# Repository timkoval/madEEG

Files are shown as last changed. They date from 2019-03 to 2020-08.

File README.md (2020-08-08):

# madEEG

This project is a fork and rebirth of an old project called "[OpenEEG](http://openeeg.sourceforge.net/doc/)".

The main feature of this project is that it uses currently available SMD components. Moreover, in the future I'm planning to try to make it cheaper using DSP instead of amplifier filters where it is possible.

I wanted to make it myself as a pet project, but unfortunately I don't have enough time and money. However, I really want this project to be developed... You are welcome to contribute!

## Requirements and tools

Schematic and PCB - [KiCAD](https://kicad-pcb.org/) 

Firmware - [STM32CubeIDE](https://www.st.com/en/development-tools/stm32cubeide.html) or any other IDE/code editor (As for me, I've recently migrated from CubeIDE to [VSCodium](https://vscodium.com/))

 Software - haven't thought about it yet, open to suggestions.

## Installation

No need to install project, just clone it, develop and contribute :) 

## Contributing

Pull requests are welcome! For major changes, please open an issue first to discuss what you would like to change.

## Authors

- **Tim Koval** - *Initial work* - [madTRACER](https://github.com/madTRACER)

## License

This project is under the MIT license.

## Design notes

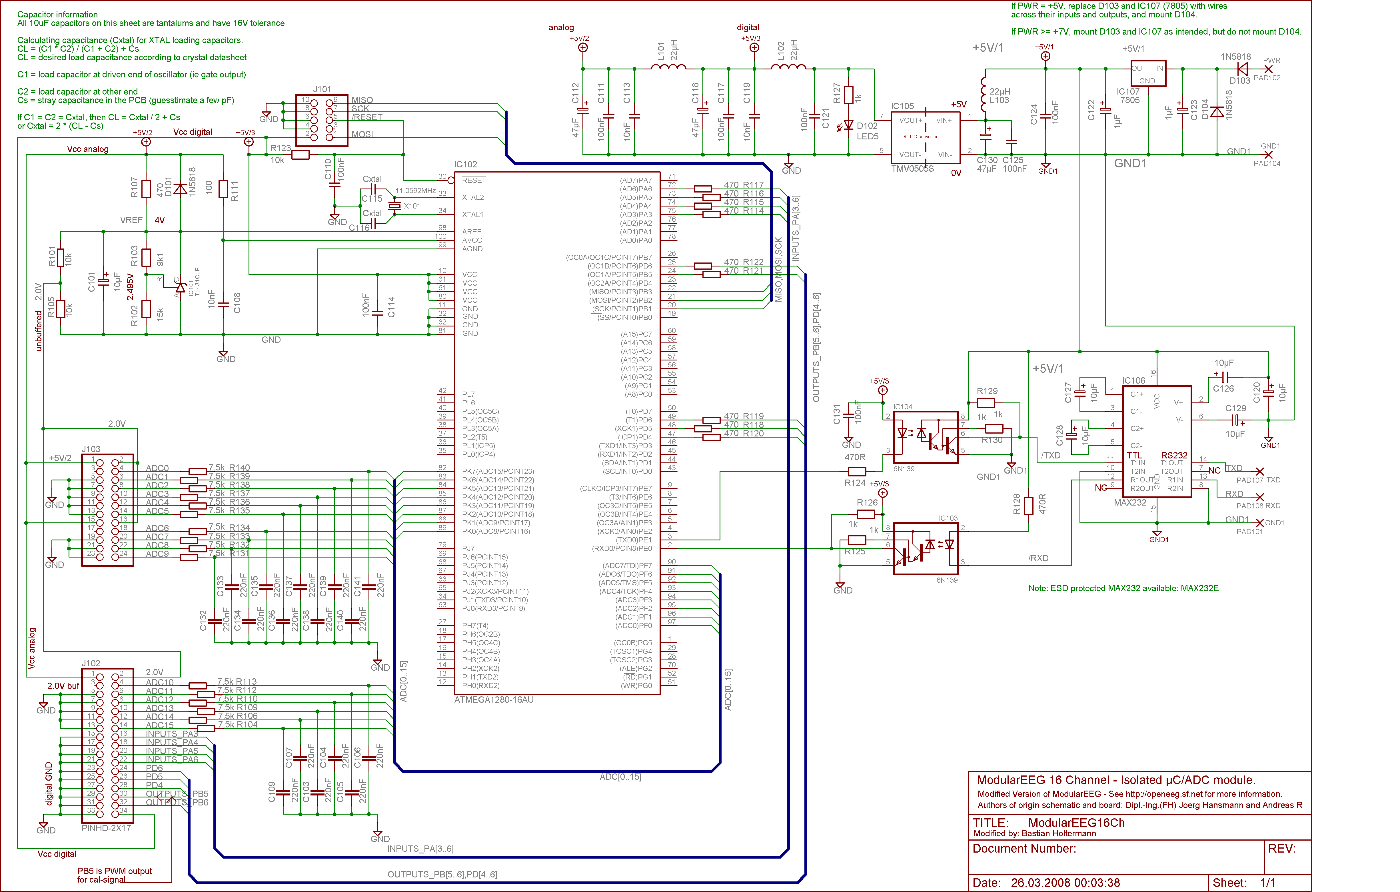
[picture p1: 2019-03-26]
REFERENCE/modeeg16ch - bastianholtermann.de - ModEEG16ch/ModularEEG16Ch.sch.png

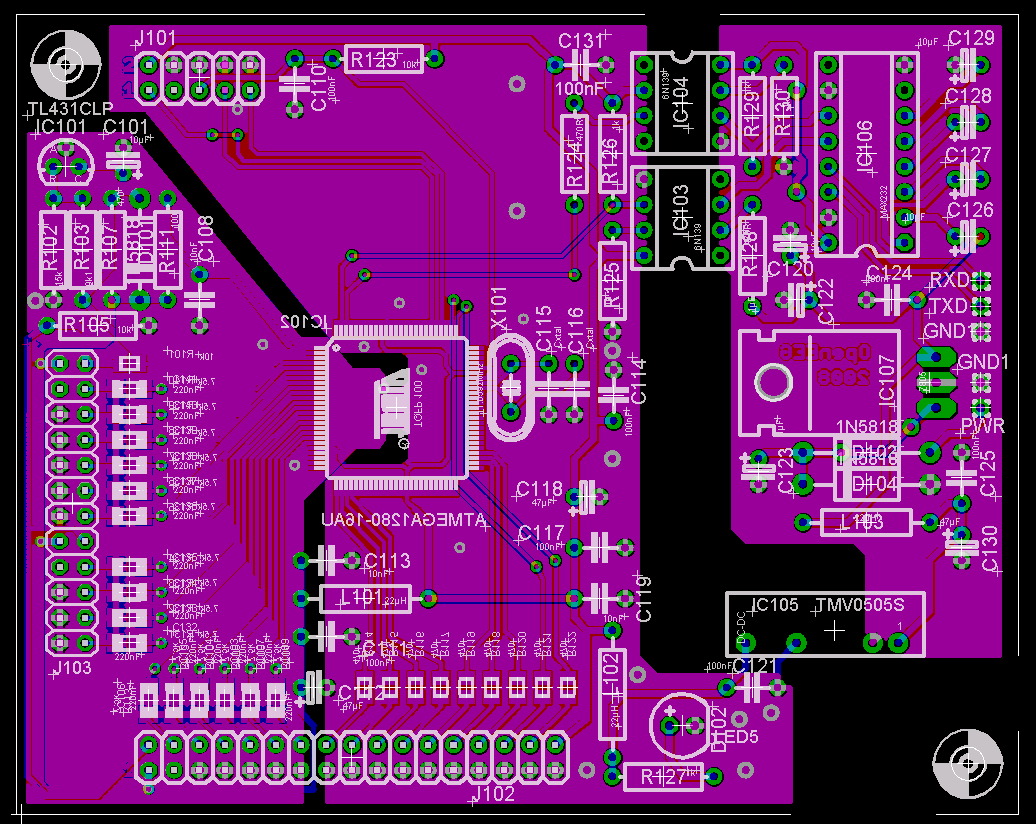
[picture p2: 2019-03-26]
REFERENCE/modeeg16ch - bastianholtermann.de - ModEEG16ch/ModularEEG16Ch.brd.png

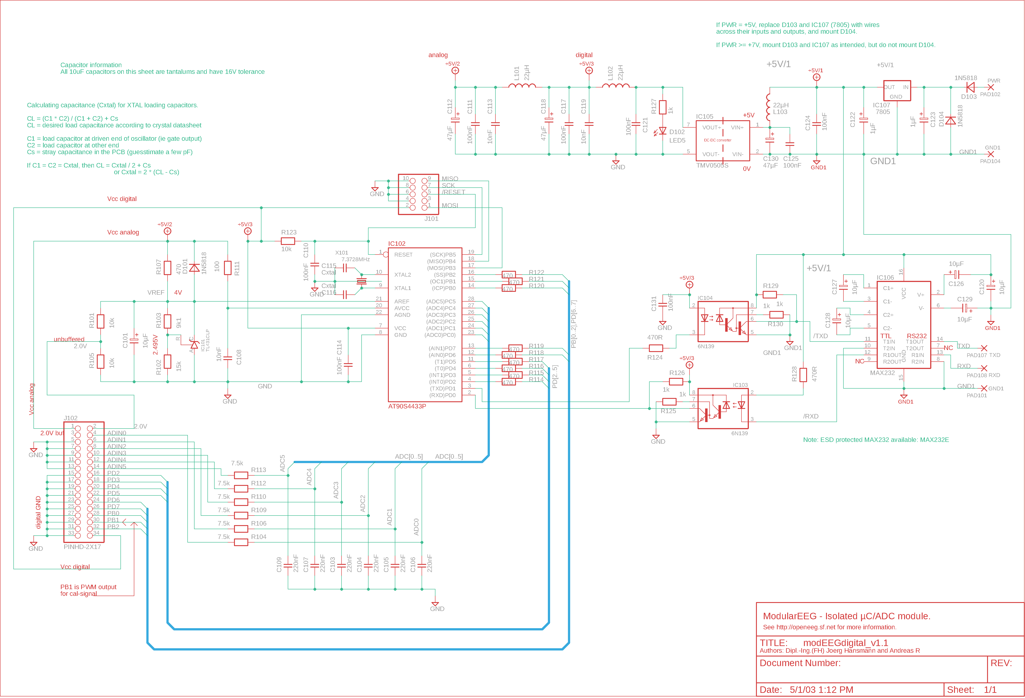
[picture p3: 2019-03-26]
REFERENCE/ModularEEG-v1.1.1/modEEGdigital_v1.1.png

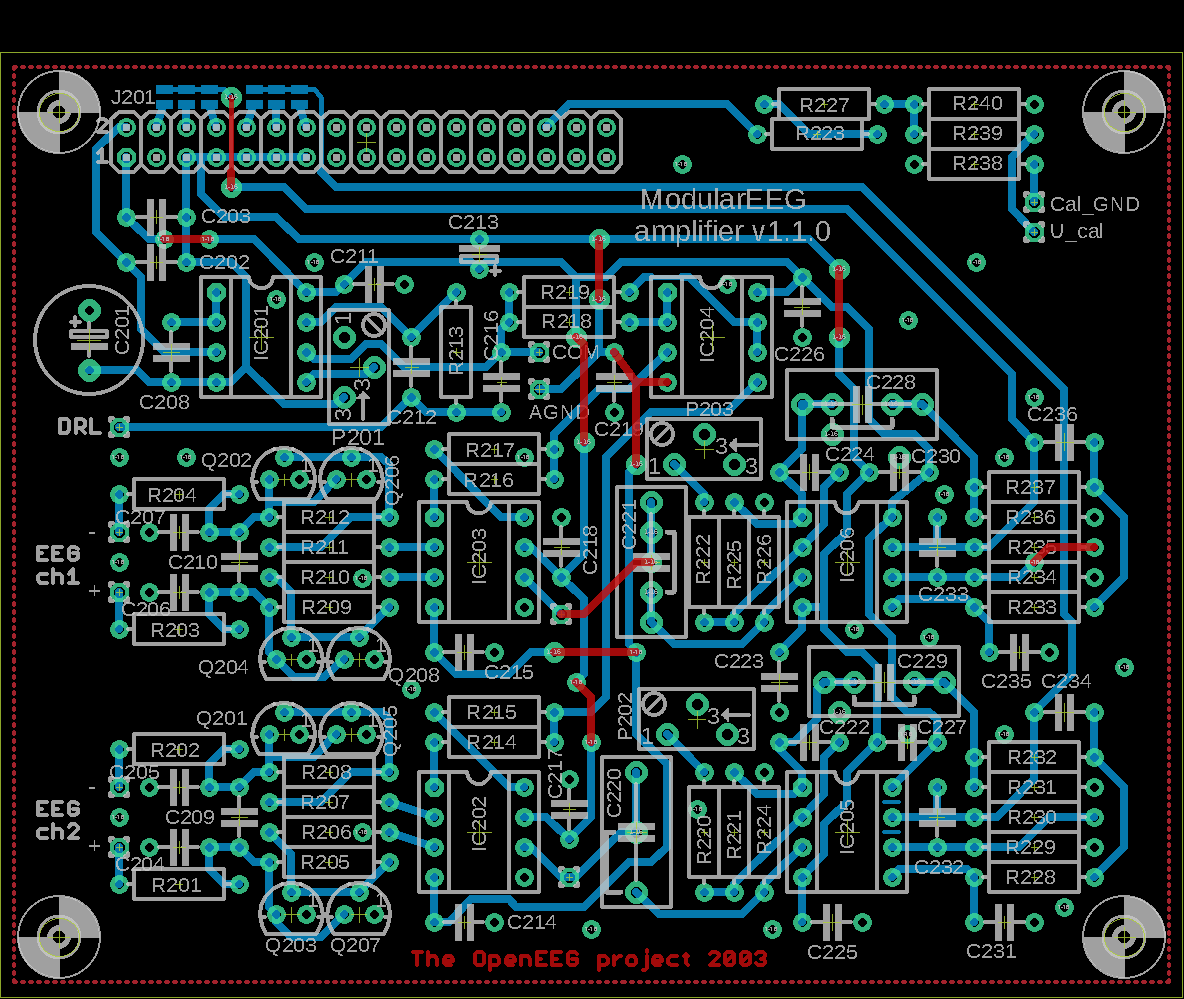
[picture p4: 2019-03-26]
REFERENCE/ModularEEG-v1.1.1/modEEGamp_v1.1_pcb.png

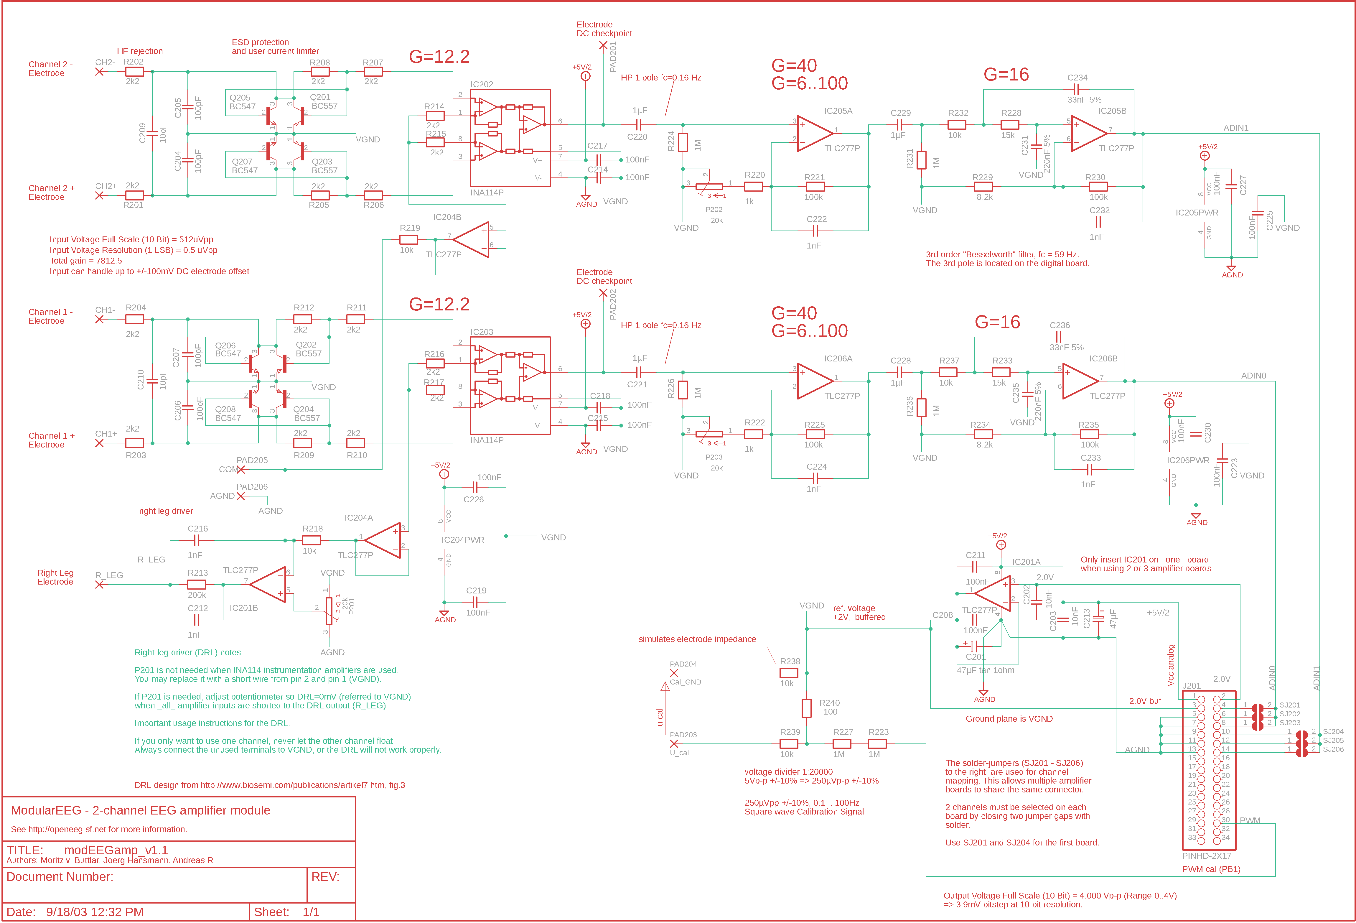
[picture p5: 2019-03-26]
REFERENCE/ModularEEG-v1.1.1/mogEEGamp_v1.1.png

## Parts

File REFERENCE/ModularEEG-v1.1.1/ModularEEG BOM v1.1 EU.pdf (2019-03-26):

# ModularEEG v1.1.0 - Bill of Materials

# Digital board

Qty | Value | Package | Parts

# Capacitors

1 | 27pF C0G | C-5 | C102
2 | Cxtal | C-5 | C115 | C116
3 | 10nF X7R | C-5 | C108 | C113 | C119
7 | 100nF X7R | C-5 | C110 | C111 | C114 | C117 | C121 | C124 | C125 | C131
6 | 220nF 5% | C-5 | C103 | C104 | C105 | C106 | C107 | C109
2 | 1µF tantalum | EL25B | C122 | C123
6 | 10µF tantalum | EL25B | C101 | C120 | C126 | C127 | C128 | C129
3 | 47µF tantalum | EL25B | C112 | C118 | C130

# Resistors

1 | 100R | R-10 | R111
12 | 470R | R-10 | R107 | R114 | R115 | R116 | R117 | R118 | R119 | R120 | R121 | R122 | R124 | R128
5 | 1k | R-10 | R125 | R126 | R127 | R129 | R130
6 | 7.5k | R-10 | R104 | R106 | R109 | R110 | R112 | R113
1 | 9k1 | R-10 | R103
3 | 10k | R-10 | R101 | R105 | R123
1 | 15k | R-10 | R102

# Discrete Semiconductors

3 | 1N5818 | D-12,5 | D101 | D103 | D104
1 | LED 5mm | LED5 | D102

# Integrated Circuits

2 | 6N139 | DIL-08 | IC103 | IC104
1 | 7805 | 78XXL_S | IC107
1 | AT90S4433P | DIL-28/3 | IC102
1 | MAX232 | DIL-16 | IC106
1 | TL431CLP | TO92-CLP | IC101
1 | TMV0505S | TMADCDC IC105

# Miscellaneous Parts

1 | 7.3728MHz | HC49/S | X101
3 | 22µH | R-12,5 | L101 | L102 | L103
1 | PINHD-2X5 | 2X05 | J101
1 | PINHD-2X17 | 2X17 | J102

# Analog board

Qty | Value | Package | Parts

# Capacitors

2 | 10pF C0G | C-5 | C209 | C210
4 | 100pF C0G | C-5 | C204 | C205 | C206 | C207
6 | 1nF X7R | C-5 | C212 | C216 | C222 | C224 | C232 | C233
2 | 10nF X7R | C-5 | C202 | C203
2 | 33nF 5% | C-5 | C234 | C236
12 | 100nF X7R | C-5 | C208 | C211 | C214 | C215 | C217 | C218 | C219 | C223 | C225 | C226 | C227 | C230
2 | 220nF 5% | C-5 | C231 | C235
4 | 1µF film | C-10 | C220 | C221 | C228 | C229
1 | 47µF tantalum | EL25B | C213
1 | 47µF tan 1ohm | ES-5 | C201

# Resistors

1 | 100R | R-10 | R240
2 | 1k | R-10 | R220 | R222
16 | 2k2 | R-10 | R201 | R202 | R203 | R204 | R205 | R206 | R207 | R208 | R209 | R210 | R211 | R212
| | | R214 | R215 | R216 | R217
2 | 8.2k | R-10 | R229 | R234
6 | 10k | R-10 | R218 | R219 | R232 | R237 | R238 | R239
2 | 15k | R-10 | R228 | R233
4 | 100k | R-10 | R221 | R225 | R230 | R235
1 | 200k | R-10 | R213
6 | 1M | R-10 | R223 | R224 | R226 | R227 | R231 | R236

# Discrete Semiconductors

4 | BC547 | TO92 | Q205 | Q206 | Q207 | Q208
4 | BC557 | TO92 | Q201 | Q202 | Q203 | Q204

# Integrated Circuits

2 | INA114P | DIL-08 | IC202 | IC203
4 | TLC277P | DIL-08 | IC201 | IC204 | IC205 | IC206

# Miscellaneous Parts

3 | 20k | S64Y | P201 | P202 | P203
1 | PINHD-2X17 | 2X17 | J201

170

# ModularEEG v1.1.0 - ordering information

All prices as of September 2002.

See notes below. No part is selected. See distributor-specific notes below.. Not available. Prices given are estimates.

| Reichelt | RS Components | Reichelt | RS Components

Color key:

Value | Package | Qty
D
| | | Qty
A
| | | | Qty D+A

Qty

| | | | | D+2A | Part requirements and notes | Part no. | Unit Price | Min
Qty | ? | Part no.
| | | | | | | | | | | Unit Price | Min
Qty | ?
| | | | | | | | | | | | | | Qty
D
| | | | | | | | | | | | | | | Qty
A
| | | | | | | | | | | | | | | | Qty D+A

Qty

| | | | | | | | | | | | | | | | | D+2A | Price
D
| | | | | | | | | | | | | | | | | | | Price
A
| | | | | | | | | | | | | | | | | | | | Price D+A | Price D+2A | Qty
D
| | | | | | | | | | | | | | | | | | | | | | | Qty
A
| | | | | | | | | | | | | | | | | | | | | | | | Qty D+A

Qty

| | | | | | | | | | | | | | | | | | | | | | | | | D+2A | Price
D
| | | | | | | | | | | | | | | | | | | | | | | | | | | Price A | Price D+A | Price D+2A
Capacitors | | | | | | | | | | | | | Capacitors
10pF C0G | C-5 | | 2 | 2 | 4 | 100V, 5mm pitch,C0G | Kerko-500 10p | 0,07 | 1 | N/A | 0,1 | 5 | 10pF C0G | | 2 | 2 | 4 | | 0,14 | 0,14 | 0,28 | | 5 | 5 | 5 | | 0,5 | 0,5 | 0,5
Cxtal C0G | C-5 | 2 | 2 | 2 5mm pitch, C0G. See notes. | Kerko-500 56p | 0,07 | 1 1 | N/A | 0,1 | 5 1 | Cxtal C0G | 2 | 2 | 2 | 0,14 | 0,14 | 0,14 | 5 | 5 | 5 | 0,5 | 0,5 | 0,5
100pF C0G | C-5 | | 4 | 4 | 8 | 100V, 5mm pitch, C0G | Kerko-500 100p | 0,07 | 1 | N/A | 0,1 | 5 | 100pF C0G | | 4 | 4 | 8 | | 0,28 | 0,28 | 0,56 | | 5 | 5 | 10 | | 0,5 | 0,5 | 1
1nF X7R | C-5 | | 6 | 6 | 12 | 200V, 5mm pitch, X7R | X7R-5 1,0n | 0,07 | 1 | 298-9028 | 0,14 | 5 | 1nF X7R | | 6 | 6 | 12 | | 0,42 | 0,42 | 0,84 | | 10 | 10 | 15 | | 1,4 | 1,4 | 2,1
10nF X7R | C-5 | 3 | 2 | 5 | 7 | 100V, 5mm pitch, X7R | X7R-5 10n | 0,07 | 1 | 264-4832 | 0,16 | 5 | 10nF X7R | 3 | 2 | 5 | 7 | 0,21 | 0,14 | 0,35 | 0,49 | 5 | 5 | 5 | 10 | 0,8 | 0,8 | 0,8 | 1,6
33nF 5% | C-5 | | 2 | 2 | 4 | 5%, 5mm pitch, max 3.5mm wide | N/A | 0,1 | 1 | 312-1504 | 0,082 | 10 | 33nF 5% | | 2 | 2 | 4 | | 0,2 | 0,2 | 0,4 | | 10 | 10 | 10 | | 0,82 | 0,82 | 0,82
100nF X7R | C-5 | 8 | 12 | 20 | 32 | 50V, 5mm pitch, X7R | X7R-5 100n | 0,12 | 1 | 264-4876 | 0,205 | 5 | 100nF X7R | 8 | 12 | 20 | 32 | 0,96 | 1,44 | 2,4 | 3,84 | 10 | 15 | 20 | 35 | 2,05 | 3,075 | 4,1 | 7,175
220nF 5% | C-5 | 6 | 2 | 8 | 10 | 5%, 5mm pitch, max 3.5mm wide | N/A | 0,2 | 1 | 312-1475 | 0,139 | 10 | 220nF 5% | 6 | 2 | 8 | 10 | 1,2 | 0,4 | 1,6 | 2 | 10 | 10 | 10 | 10 | 1,39 | 1,39 | 1,39 | 1,39
1µF film | C-10 | | 4 | 4 | 8 | 5% tolerance, 10mm pitch | MKH100-10 1,0µ | 0,3 | 1 | 298-0188 | 0,349 | 5 | 1µF film | | 4 | 4 | 8 | | 1,2 | 1,2 | 2,4 | | 5 | 5 | 10 | | 1,745 | 1,745 | 3,49
1µF tantalum | EL25B | 2 | | 2 | 2 | 35V, 2.5mm pitch | TANTAL 1,0/35 | 0,15 | 1 | N/A | 0,2 | 1 | 1µF tantalum | 2 | | 2 | 2 | 0,3 | | 0,3 | 0,3 | 2 | | 2 | 2 | 0,4 | | 0,4 | 0,4
10µF tantalum | EL25B | 6 | | 6 | 6 | 16V, 2.5mm pitch | TANTAL 10/16 | 0,22 | 1 | N/A | 0,2 | 1 | 10µF tantalum | 6 | | 6 | 6 | 1,32 | | 1,32 | 1,32 | 6 | | 6 | 6 | 1,2 | | 1,2 | 1,2
47µF tantalum | EL25B | 3 | 1 | 4 | 5 | > 6.3V, 2.5mm pitch | TANTAL 47/6,3 | 0,33 | 1 | N/A | 0,3 | 1 | 47µF tantalum | 3 | 1 | 4 | 5 | 0,99 | 0,33 | 1,32 | 1,65 | 3 | 1 | 4 | 5 | 0,9 | 0,3 | 1,2 | 1,5
47µF tan 1ohm | ES-5 | 1 | 1 | 2 > 6.3V, 5mm pitch, ESR = 0.8 - 1.2 ohm | N/A | 3 | 1 | N/A | 3 | 1 | 47µF tan 1ohm | 1 | 1 | 2 | 3 | 3 | 6 | 1 | 1 | 2 | 3 | 3 | 6
Resistors | | | | | | | | | | | | | Resistors
100R | R-10 | 1 | 1 | 2 | 3 | 1% metal film, 0.25W, 10mm pitch | METALL 100 | 0,08 | 1 | 148-269 | 0,044 | 10 | 100R | 1 | 1 | 2 | 3 | 0,08 | 0,08 | 0,16 | 0,24 | 10 | 10 | 10 | 10 | 0,44 | 0,44 | 0,44 | 0,44
470R | R-10 | 12 | | 12 | 12 | 1% metal film, 0.25W, 10mm pitch | METALL 470 | 0,08 | 1 | 148-427 | 0,044 | 10 | 470R | 12 | | 12 | 12 | 0,96 | | 0,96 | 0,96 | 20 | | 20 | 20 | 0,88 | | 0,88 | 0,88
1k | R-10 | 5 | 2 | 7 | 9 | 1% metal film, 0.25W, 10mm pitch | METALL 1,00K | 0,08 | 1 | 148-506 | 0,044 | 10 | 1k | 5 | 2 | 7 | 9 | 0,4 | 0,16 | 0,56 | 0,72 | 10 | 10 | 10 | 10 | 0,44 | 0,44 | 0,44 | 0,44
2k2 | R-10 | | 16 | 16 | 32 | 1% metal film, 0.25W, 10mm pitch | METALL 2,20K | 0,08 | 1 | 148-584 | 0,044 | 10 | 2k2 | | 16 | 16 | 32 | | 1,28 | 1,28 | 2,56 | | 20 | 20 | 40 | | 0,88 | 0,88 | 1,76
7.5k | R-10 | 6 | | 6 | 6 | 1% metal film, 0.25W, 10mm pitch | METALL 7,50K | 0,08 | 1 | 148-708 | 0,044 | 10 | 7.5k | 6 | | 6 | 6 | 0,48 | | 0,48 | 0,48 | 10 | | 10 | 10 | 0,44 | | 0,44 | 0,44
8.2k | R-10 | | 2 | 2 | 4 | 1% metal film, 0.25W, 10mm pitch | METALL 8,20K | 0,08 | 1 | 148-714 | 0,044 | 10 | 8.2k | | 2 | 2 | 4 | | 0,16 | 0,16 | 0,32 | | 10 | 10 | 10 | | 0,44 | 0,44 | 0,44
9k1 | R-10 | 1 | | 1 | 1 | 1% metal film, 0.25W, 10mm pitch | METALL 9,10K | 0,08 | 1 | 148-720 | 0,044 | 10 | 9k1 | 1 | | 1 | 1 | 0,08 | | 0,08 | 0,08 | 10 | | 10 | 10 | 0,44 | | 0,44 | 0,44
10k | R-10 | 3 | 6 | 9 | 15 | 1% metal film, 0.25W, 10mm pitch | METALL 10,0K | 0,08 | 1 | 148-736 | 0,044 | 10 | 10k | 3 | 6 | 9 | 15 | 0,24 | 0,48 | 0,72 | 1,2 | 10 | 10 | 10 | 20 | 0,44 | 0,44 | 0,44 | 0,88
15k | R-10 | 1 | 2 | 3 | 5 | 1% metal film, 0.25W, 10mm pitch | METALL 15,0K | 0,08 | 1 | 148-770 | 0,044 | 10 | 15k | 1 | 2 | 3 | 5 | 0,08 | 0,16 | 0,24 | 0,4 | 10 | 10 | 10 | 10 | 0,44 | 0,44 | 0,44 | 0,44
100k | R-10 | | 4 | 4 | 8 | 1% metal film, 0.25W, 10mm pitch | METALL 100K | 0,08 | 1 | 148-972 | 0,044 | 10 | 100k | | 4 | 4 | 8 | | 0,32 | 0,32 | 0,64 | | 10 | 10 | 10 | | 0,44 | 0,44 | 0,44
200k | R-10 | | 1 | 1 | 2 | 1% metal film, 0.25W, 10mm pitch | METALL 200K | 0,08 | 1 | 149-054 | 0,044 | 10 | 200k | | 1 | 1 | 2 | | 0,08 | 0,08 | 0,16 | | 10 | 10 | 10 | | 0,44 | 0,44 | 0,44
1M | R-10 | | 6 | 6 | 12 | 1% metal film, 0.25W, 10mm pitch | METALL 1,00M | 0,08 | 1 | 149-228 | 0,044 | 10 | 1M | | 6 | 6 | 12 | | 0,48 | 0,48 | 0,96 | | 10 | 10 | 20 | | 0,44 | 0,44 | 0,88
Discrete Semiconductors | | | | | | | | | | | | | Discrete Semiconductors
1N5818 | D-12,5 | 3 | | 3 | 3 | Any 1A schottky should work. | 1N 5818 | 0,06 | 1 | 348-5505 | 0,12 | 1 | | 1N5818 | 3 | | 3 | 3 | 0,18 | | 0,18 | 0,18 | 3 | | 3 | 3 | 0,36 | | 0,36 | 0,36
BC547 | TO92 | | 4 | 4 | 8 | TO92 | BC 547B | 0,05 | 1 | 348-9399 | 0,043 | 1 | | BC547 | | 4 | 4 | 8 | | 0,2 | 0,2 | 0,4 | | 4 | 4 | 8 | | 0,172 | 0,172 | 0,344
BC557 | TO92 | 4 | 4 | 8 | TO92 | BC 557B | 0,05 | 1 | 348-9456 | 0,043 | 1 | BC557 | 4 | 4 | 8 | 0,2 | 0,2 | 0,4 | 4 | 4 | 8 | 0,172 | 0,172 | 0,344
LED 5mm | LED5 | 1 | 1 | 1 | Any LED | 0,3 | 1 | 0,3 | 1 | LED 5mm | 1 | 1 | 1 | 0,3 | 0,3 | 0,3 | 1 | 1 | 1 | 0,3 | 0,3 | 0,3
Integrated Circuits | | | | | | | | | | | | Integrated Circuits
6N139 | DIL-08 | 2 | 2 | 2 | Optocoupler | 6N139 | 0,69 | 1 | 303-135 | 1,18 | 1 | | 6N139 | 2 | 2 | 2 | 1,38 | 1,38 | 1,38 | 2 | 2 | 2 | 2,36 | 2,36 | 2,36
7805 | 78XXL_S | 1 | 1 | 1 | 5V regulator, >= 500mA. Size TO220 | µA 7805 | 0,28 | 1 | 633-026 | 0,575 | 1 | 7805 | 1 | 1 | 1 | 0,28 | 0,28 | 0,28 | 1 | 1 | 1 | 0,575 | 0,575 | 0,575
AT90S4433P | DIL-28/3 | 1 | 1 | 1 Will be replaced by ATmega8 soon. | AT 90S4433 PDIP | 7,5 | 1 | N/A | 7,5 | 1 | AT90S4433P | 1 | 1 | 1 | 7,5 | 7,5 | 7,5 | 1 | 1 | 1 | 7,5 | 7,5 | 7,5
INA114AP | DIL-08 | 2 | 2 | 4 | Low-power precision inamp | INA 114AP | 7,85 | 1 2 | 311-524 | 7,86 | 1 | INA114AP | 2 | 2 | 4 | 15,7 | 15,7 | 31,4 | 2 | 2 | 4 | 15,72 | 15,72 | 31,44
MAX232 | DIL-16 | 1 | 1 | 1 | RS232 tranceiver | MAX 232 CPE | 1 | 1 3 | 225-8510 | 1,74 | 1 | MAX232 | 1 | 1 | 1 | 1 | 1 | 1 | 1 | 1 | 1 | 1,74 | 1,74 | 1,74
TL431CLP | TO92-CLP | 1 | 1 | 1 | Adjustable voltage reference | TL 431 ACLP | 0,3 | 1 | 267-9995 | 0,39 | 1 | TL431CLP | 1 | 1 | 1 | 0,3 | 0,3 | 0,3 | 1 | 1 | 1 | 0,39 | 0,39 | 0,39
TLC277P | DIL-08 | 4 | 4 | 7 Dual precision opamp | TLC 277 DIP | 1,65 | 1 | 428-464 | 1,785 | 1 | TLC277P | 4 | 4 | 7 | 6,6 | 6,6 | 11,55 | 4 | 4 | 7 | 7,14 | 7,14 | 12,5
TMV0505S | TMADCDC | 1 | 1 | 1 5Vin-5Vout 10% SIP7, 3kV iso | N/A | 10 | 1 | 192-0826 | 10,7 | 1 3 | TMV0505S | 1 | 1 | 1 | 10 | 10 | 10 | 1 | 1 | 1 | 10,7 | 10,7 | 10,7
Miscellaneous Parts | | | | | | | | | | | | Miscellaneous Parts
20k | S64Y | 3 | 3 | 6 | Multi-turn trimpot, 64Y footprint | 64Y-20K | 0,64 | 1 | 154-2448 | 1,476 | 1 | | 20k | 3 | 3 | 6 | 1,92 | 1,92 | 3,84 | 3 | 3 | 6 | 4,428 | 4,428 | 8,856
22µH | R-12,5 | 3 | 3 | 3 | SRF > 13MHz, Imax > 285mA, 12.5mm pitch | SMCC 22µ | 0,19 | 1 | 191-0526 | 0,225 | 10 | 22µH | 3 | 3 | 3 | 0,57 | 0,57 | 0,57 | 10 | 10 | 10 | 2,25 | 2,25 | 2,25
7.3728MHz | HC49/S | 1 | 1 | 1 HC49 or equivalent package. | 7,3728-HC49U-S | 0,49 | 1 1 | 311-811 | 1,23 | 1 1 | 7.3728MHz | 1 | 1 | 1 | 0,49 | 0,49 | 0,49 | 1 | 1 | 1 | 1,23 | 1,23 | 1,23
PINHD-2X17 | 2X17 | 1 | 1 | 2 | 3 2x17 pin-header / ribbon cable connector | STIFTL. 2X17G | 0,21 | 1 | 2 | PINHD-2X17 | 1 | 1 | 2 | 3 | 0,21 | 0,21 | 0,42 | 0,63
PINHD-2X5 | 2X05 | 1 | 1 | 1 2x5 pin-header / ribbon cable connector | STIFTL. 2X17G | 0,21 | 1 | 2 | PINHD-2X5 | 1 | 1 | 1 | 0,21 | 0,21 | 0,21
Sockets | | | | | | | | | | | | Sockets
8-pin socket | DIL-08 | 2 | 6 | 8 | 14 | GS 8 | 0,03 | 1 | Very expensive | 8-pin socket | 2 | 6 | 8 | 14 | 0,06 | 0,18 | 0,24 | 0,42
16-pin socket | DIL-16 | 1 | 1 | 1 | GS 16 | 0,04 | 1 | since minimum | 16-pin socket | 1 | 1 | 1 | 0,04 | 0,04 | 0,04
28-pin socket | DIL-28 | 1 | 1 | 1 | 7.68mm wide. | GS 14 | 0,04 | 2 4 | order is 50 pieces. | 28-pin socket | 2 | 2 | 2 | 0,08 | 0,08 | 0,08
Socket strip | SIL-20 | | | | Can be useful... | | | | 267-7400 | 0,55 | 5 | Socket strip

Notes

Crystal and loading capacitors (Cxtal)
The crystal's loading capacitors must be chosen appropriately. Set Cxtal = (Cload - Cstray) * 2
Cload (crystal loading capacitance) is given in the crystal data sheet. Cstray is stray capacitance on the PCB + microcontroller. Estimate Cstray = 3 - 5pF.

47uF 1 ohm capacitor
This capacitor is hard to locate in through-hole form (unless you order from Newark) You can replace it with an SMD type.
Mount an SMD like this: Solder the negative end to its pad. Have the positive end land on the ground plane. Scrape off the solder mask
in front of the positive end and solder.
Also note that any ESR = 0.8 ohm to 1.2 ohm is acceptable.

Microcontroller
The AT90S4433 is "not recommended for new designs" which is industry-speak for "we are not going to manufacture this part for much longer". The replacement is the ATmega8. However, it has a problem associated with it:
ADC channels 5 and 6 are only 8 bit, while the EEG board is designed with 10 bit resolution in mind. (Channels 1 - 4 are ok though.)

TLC277 amplifier
In a four channel EEG setup (two amplifier boards), you only mount IC201 on one board.

DCDC converter
TMV0505S is not available in many places. It can be replaced with NMV0505SA. This converter has a rather high output voltage (6-7 V) at very light loads. Therefore, when building the digital board, mount all parts except the microcontroller. Turn on the power and measure the voltage in the +5V/3 net, e.g. at IC103 pin 8. The voltage should be LESS than 6V. If not, you must reduce the value of R127 (near the LED), in order to present the DCDC converter with a higher load.

Pin headers
These are fairly expensive at RS (order code 531-942, you need 17x2 + 17x2 + 3x2 = 74 pins total) so try to find them elsewhere.
You need 2.54mm pitch double-row headers or equialent connectors, for ribbon cable. The ribbon cable can be made from an old floppy-drive cable.

Socket strip
Instead of soldering wires directly to the PCB's you can solder in socket strips which you have cut into suitable lengths.
Then insert the wires into the sockets without soldering, during the testing phase. This way you do not risk breaking the wires before putting everything securely in a box. (Then you should solder them in.) 0.5mm diameter single-strand wire is suitable.

Reichelt notes
1) Crystal loading capacitance is 32pF so Cxtal = 56pF (estimate Cstray = 4pF)
2) Higher grade is available: INA114BP which costs €13.60. Note that for this application this is hardly needed.
3) The MAX232 listed does not have ESD protected I/O pins. Protected type has part no MAX232 ECPE and costs €4.80.
4) Two 14-pin sockets

RS components notes
Prices were calculated from SEK to Euros by dividing by ten but at the time of writing 1 EUR = 9 SEK. Also, VAT is not included.
1) Crystal loading capacitance is 7pF so Cxtal = 10pF (estimate Cstray = 5 pF)
2) Avoid buying these parts from here. They are more expensive than they need to be.
3) TMV0505S is replaced by NMV0505SA

Newark Electronics notes
1) Crystal loading capacitance is 20pF so Cxtal = 33pF (estimate Cstray = 4pF)
2) The part has 2.5mm lead pitch - bend to 5mm
3) The part has 5mm lead pitch rather than 10mm. C220 can be mounted two ways. The lower placement (seen PCB layout) is the correct one.
4) This part may be replaced with a small aluminium electroytic. Part no 18C4465 for $0.063
5) Digital board capacitors can be replaced by an aluminium electrolytics. This may degrade noise immunity. (Probably not). Part no 18C4469 for $0.147
6) ESR=1.2 Ohm. Can be replaced with an ESR=1.0 Ohm type. Part no 87F5155 for $4.78
7)
8)
9) Higher grade INA114BP is available. Part no 35C1716 for $12.08
10) A cheaper alternative is MAX232 CPE that lacks ESD protection. Part no 34C3833 for $2.91
11) TMV0505S is replaced by NMV0505SA

Digi-Key notes
1) Carbon resistor for possibly improved ESR protection
2) Can be replaced with the newer generation ATMEGA8-16PI-ND $6.33 see Microcontroller note above.
3) Higher grade: INA114BP-ND $10.28
4) Or S2212-17-ND tin $1.77 - a special order item

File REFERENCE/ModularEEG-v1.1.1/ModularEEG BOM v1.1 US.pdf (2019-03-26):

# ModularEEG v1.1.0 - Bill of Materials

# Digital board

Qty | Value | Package | Parts

# Capacitors

1 | 27pF C0G | C-5 | C102
2 | Cxtal | C-5 | C115 | C116
3 | 10nF X7R | C-5 | C108 | C113 | C119
7 | 100nF X7R | C-5 | C110 | C111 | C114 | C117 | C121 | C124 | C125 | C131
6 | 220nF 5% | C-5 | C103 | C104 | C105 | C106 | C107 | C109
2 | 1µF tantalum | EL25B | C122 | C123
6 | 10µF tantalum | EL25B | C101 | C120 | C126 | C127 | C128 | C129
3 | 47µF tantalum | EL25B | C112 | C118 | C130

# Resistors

1 | 100R | R-10 | R111
12 | 470R | R-10 | R107 | R114 | R115 | R116 | R117 | R118 | R119 | R120 | R121 | R122 | R124 | R128
5 | 1k | R-10 | R125 | R126 | R127 | R129 | R130
6 | 7.5k | R-10 | R104 | R106 | R109 | R110 | R112 | R113
1 | 9k1 | R-10 | R103
3 | 10k | R-10 | R101 | R105 | R123
1 | 15k | R-10 | R102

# Discrete Semiconductors

3 | 1N5818 | D-12,5 | D101 | D103 | D104
1 | LED 5mm | LED5 | D102

# Integrated Circuits

2 | 6N139 | DIL-08 | IC103 | IC104
1 | 7805 | 78XXL_S | IC107
1 | AT90S4433P | DIL-28/3 | IC102
1 | MAX232 | DIL-16 | IC106
1 | TL431CLP | TO92-CLP | IC101
1 | TMV0505S | TMADCDC IC105

# Miscellaneous Parts

1 | 7.3728MHz | HC49/S | X101
3 | 22µH | R-12,5 | L101 | L102 | L103
1 | PINHD-2X5 | 2X05 | J101
1 | PINHD-2X17 | 2X17 | J102

# Analog board

Qty | Value | Package | Parts

# Capacitors

2 | 10pF C0G | C-5 | C209 | C210
4 | 100pF C0G | C-5 | C204 | C205 | C206 | C207
6 | 1nF X7R | C-5 | C212 | C216 | C222 | C224 | C232 | C233
2 | 10nF X7R | C-5 | C202 | C203
2 | 33nF 5% | C-5 | C234 | C236
12 | 100nF X7R | C-5 | C208 | C211 | C214 | C215 | C217 | C218 | C219 | C223 | C225 | C226 | C227 | C230
2 | 220nF 5% | C-5 | C231 | C235
4 | 1µF film | C-10 | C220 | C221 | C228 | C229
1 | 47µF tantalum | EL25B | C213
1 | 47µF tan 1ohm | ES-5 | C201

# Resistors

1 | 100R | R-10 | R240
2 | 1k | R-10 | R220 | R222
16 | 2k2 | R-10 | R201 | R202 | R203 | R204 | R205 | R206 | R207 | R208 | R209 | R210 | R211 | R212
| | | R214 | R215 | R216 | R217
2 | 8.2k | R-10 | R229 | R234
6 | 10k | R-10 | R218 | R219 | R232 | R237 | R238 | R239
2 | 15k | R-10 | R228 | R233
4 | 100k | R-10 | R221 | R225 | R230 | R235
1 | 200k | R-10 | R213
6 | 1M | R-10 | R223 | R224 | R226 | R227 | R231 | R236

# Discrete Semiconductors

4 | BC547 | TO92 | Q205 | Q206 | Q207 | Q208
4 | BC557 | TO92 | Q201 | Q202 | Q203 | Q204

# Integrated Circuits

2 | INA114P | DIL-08 | IC202 | IC203
4 | TLC277P | DIL-08 | IC201 | IC204 | IC205 | IC206

# Miscellaneous Parts

3 | 20k | S64Y | P201 | P202 | P203
1 | PINHD-2X17 | 2X17 | J201

170

# ModularEEG v1.1.0 - ordering information

All prices as of September 2002.

See notes below. No part is selected. See distributor-specific notes below.. Not available. Prices given are estimates.

| | | | | | | Newark Electronics | | Digi-Key (USD) | | | | Newark Electronics | | Digi-Key
Value | Package | Qty D | Qty A | Qty D+A | Qty D+2A | Part requirements and notes | Part no. | Unit Price | Min Qty | ? | Part no. | Unit Price | Min Qty | ? | | Qty D | Qty A | Qty D+A | Qty D+2A | Price D | Price A | Price D+A | Price D+2A | Qty D | Qty A | Qty D+A | Qty D+2A | Price D | Price A | Price D+A | Price D+2A

Color key:

Capacitors | | | | | | | | | | Capacitors
10pF C0G | C-5 | | 2 | 2 | 4 | 100V, 5mm pitch,C0G | 50N1022 | 0,044 | 1 | 10pF C0G | | 2 | 2 | 4 | | 0,088 | 0,088 | 0,176
Cxtal C0G | C-5 | 2 | 2 | 2 5mm pitch, C0G. See notes. | 50N1028 | 0,044 | 1 1 | Cxtal C0G | 2 | 2 | 2 | 0,088 | 0,088 | 0,088
100pF C0G | C-5 | | 4 | 4 | 8 | 100V, 5mm pitch, C0G | 50N1068 | 0,044 | 1 | 100pF C0G | | 4 | 4 | 8 | | 0,176 | 0,176 | 0,352
1nF X7R | C-5 | | 6 | 6 | 12 | 200V, 5mm pitch, X7R | 87F4719 | 0,142 | 1 2 | 1nF X7R | | 6 | 6 | 12 | | 0,852 | 0,852 | 1,704
10nF X7R | C-5 | 3 | 2 | 5 | 7 | 100V, 5mm pitch, X7R | 87F4724 | 0,123 | 1 | 10nF X7R | 3 | 2 | 5 | 7 | 0,369 | 0,246 | 0,615 | 0,861
33nF 5% | C-5 | | 2 | 2 | 4 | 5%, 5mm pitch, max 3.5mm wide | 18C4841 | 0,236 | 1 | 33nF 5% | | 2 | 2 | 4 | | 0,472 | 0,472 | 0,944
100nF X7R | C-5 | 8 | 12 | 20 | 32 | 50V, 5mm pitch, X7R | 96F8771 | 0,122 | 1 | 100nF X7R | 8 | 12 | 20 | 32 | 0,976 | 1,464 | 2,44 | 3,904
220nF 5% | C-5 | 6 | 2 | 8 | 10 | 5%, 5mm pitch, max 3.5mm wide | 95B5780 | 0,108 | 1 | 220nF 5% | 6 | 2 | 8 | 10 | 0,648 | 0,216 | 0,864 | 1,08
1µF film | C-10 | | 4 | 4 | 8 | 5% tolerance, 10mm pitch | 95B5792 | 0,325 | 1 3 | 1µF film | | 4 | 4 | 8 | | 1,3 | 1,3 | 2,6
1µF tantalum | EL25B | 2 | | 2 | 2 | 35V, 2.5mm pitch | 50N905 | 0,235 | 1 | 1µF tantalum | 2 | | 2 | 2 | 0,47 | | 0,47 | 0,47
10µF tantalum | EL25B | 6 | | 6 | 6 | 16V, 2.5mm pitch | 50N883 | 0,459 | 1 4 | 10µF tantalum | 6 | | 6 | 6 | 2,754 | | 2,754 | 2,754
47µF tantalum | EL25B | 3 | 1 | 4 | 5 | > 6.3V, 2.5mm pitch | 50N860 | 0,683 | 1 5 | 47µF tantalum | 3 | 1 | 4 | 5 | 2,049 | 0,683 | 2,732 | 3,415
47µF tan 1ohm | ES-5 | 1 | 1 | 2 > 6.3V, 5mm pitch, ESR = 0.8 - 1.2 ohm | 95F4832 | 2,96 | 1 6 | 47µF tan 1ohm | 1 | 1 | 2 | 2,96 | 2,96 | 5,92
Resistors | | | | | | | | | | | | | Resistors
100R | R-10 | 1 | 1 | 2 | 3 | 1% metal film, 0.25W, 10mm pitch | 84N1686 | 0,031 | 1 | | | | 100R | 1 | 1 | 2 | 3 | 0,031 | 0,031 | 0,062 | 0,093
470R | R-10 | 12 | | 12 | 12 | 1% metal film, 0.25W, 10mm pitch | 84N1765 | 0,031 | 1 | | | | 470R | 12 | | 12 | 12 | 0,372 | | 0,372 | 0,372
1k | R-10 | 5 | 2 | 7 | 9 | 1% metal film, 0.25W, 10mm pitch | 84N1712 | 0,031 | 1 | | | | 1k | 5 | 2 | 7 | 9 | 0,155 | 0,062 | 0,217 | 0,279
2k2 | R-10 | | 16 | 16 | 32 | 1% metal film, 0.25W, 10mm pitch | 84N1737 | 0,031 | 1 | | | | 2k2 | | 16 | 16 | 32 | | 0,496 | 0,496 | 0,992
7.5k | R-10 | 6 | | 6 | 6 | 1% metal film, 0.25W, 10mm pitch | 84N1794 | 0,031 | 1 | | | | 7.5k | 6 | | 6 | 6 | 0,186 | | 0,186 | 0,186
8.2k | R-10 | | 2 | 2 | 4 | 1% metal film, 0.25W, 10mm pitch | 84N1799 | 0,031 | 1 | | | | 8.2k | | 2 | 2 | 4 | | 0,062 | 0,062 | 0,124
9k1 | R-10 | 1 | | 1 | 1 | 1% metal film, 0.25W, 10mm pitch | 84N1804 | 0,031 | 1 | | | | 9k1 | 1 | | 1 | 1 | 0,031 | | 0,031 | 0,031
10k | R-10 | 3 | 6 | 9 | 15 | 1% metal film, 0.25W, 10mm pitch | 84N1687 | 0,031 | 1 | | | | 10k | 3 | 6 | 9 | 15 | 0,093 | 0,186 | 0,279 | 0,465
15k | R-10 | 1 | 2 | 3 | 5 | 1% metal film, 0.25W, 10mm pitch | 84N1702 | 0,031 | 1 | | | | 15k | 1 | 2 | 3 | 5 | 0,031 | 0,062 | 0,093 | 0,155
100k | R-10 | | 4 | 4 | 8 | 1% metal film, 0.25W, 10mm pitch | 84N1685 | 0,031 | 1 | OD204J-ND | 0,42 | 1 1 | 100k | | 4 | 4 | 8 | | 0,124 | 0,124 | 0,248
200k | R-10 | | 1 | 1 | 2 | 1% metal film, 0.25W, 10mm pitch | 84N1720 | 0,031 | 1 | | | | 200k | | 1 | 1 | 2 | | 0,031 | 0,031 | 0,062 | 1 | 1 | 2 | 0,42 | 0,42 | 0,84
1M | R-10 | 6 | 6 | 12 | 1% metal film, 0.25W, 10mm pitch | 84N1719 | 0,033 | 1 | 1M | 6 | 6 | 12 | 0,198 | 0,198 | 0,396
Discrete Semiconductors | | | | | | | | | | Discrete Semiconductors
1N5818 | D-12,5 | 3 | | 3 | 3 | Any 1A schottky should work. | 09F4475 | 0,203 | 1 | | 1N5818 | 3 | | 3 | 3 | 0,609 | | 0,609 | 0,609
BC547 | TO92 | | 4 | 4 | 8 | TO92 | 92B7164 | 0,09 | 1 | | BC547 | | 4 | 4 | 8 | | 0,36 | 0,36 | 0,72
BC557 | TO92 | 4 | 4 | 8 | TO92 | 18C5843 | 0,1 | 1 | BC557 | 4 | 4 | 8 | 0,4 | 0,4 | 0,8
LED 5mm | LED5 | 1 | 1 | 1 | Any LED | 0,3 | 1 | LED 5mm | 1 | 1 | 1 | 0,3 | 0,3 | 0,3
Integrated Circuits | | | | | | | | | | | | Integrated Circuits
6N139 | DIL-08 | 2 | 2 | 2 | Optocoupler | 09F7263 | 0,918 | 1 | 6N139QT-ND | 0,95 | 1 | | 6N139 | 2 | 2 | 2 | 1,836 | 1,836 | 1,836 | 2 | 2 | 2 | 1,9 | 1,9 | 1,9
7805 | 78XXL_S | 1 | 1 | 1 | 5V regulator, >= 500mA. Size TO220 | 34C1092 | 0,6 | 1 | LM7805CT-ND | 0,48 | 1 | 7805 | 1 | 1 | 1 | 0,6 | 0,6 | 0,6 | 1 | 1 | 1 | 0,48 | 0,48 | 0,48
AT90S4433P | DIL-28/3 | 1 | 1 | 1 Will be replaced by ATmega8 soon. | N/A | 6,62 | 1 | AT90S4433-8PI-ND | 6,62 | 1 2 | AT90S4433P | 1 | 1 | 1 | 6,62 | 6,62 | 6,62 | 1 | 1 | 1 | 6,62 | 6,62 | 6,62
INA114AP | DIL-08 | 2 | 2 | 4 | Low-power precision inamp | 35C0480 | 8,02 | 1 9 | INA114AP-ND | 6,82 | 1 3 | INA114AP | 2 | 2 | 4 | 16,04 | 16,04 | 32,08 | 2 | 2 | 4 | 13,64 | 13,64 | 27,28
MAX232 | DIL-16 | 1 | 1 | 1 | RS232 tranceiver | 34C3836 | 3,68 | 1 10 | 296-6940-5-ND | 2,2 | 1 | MAX232 | 1 | 1 | 1 | 3,68 | 3,68 | 3,68 | 1 | 1 | 1 | 2,2 | 2,2 | 2,2
TL431CLP | TO92-CLP | 1 | 1 | 1 | Adjustable voltage reference | 08F9432 | 0,427 | 1 | 296-1290-ND | 0,56 | 1 | TL431CLP | 1 | 1 | 1 | 0,427 | 0,427 | 0,427 | 1 | 1 | 1 | 0,56 | 0,56 | 0,56
TLC277P | DIL-08 | 4 | 4 | 7 Dual precision opamp | 08F9096 | 1,67 | 1 | 296-1828-5-ND | 1,55 | 1 | TLC277P | 4 | 4 | 7 | 6,68 | 6,68 | 11,69 | 4 | 4 | 7 | 6,2 | 6,2 | 10,85
TMV0505S | TMADCDC | 1 | 1 | 1 5Vin-5Vout 10% SIP7, 3kV iso | 83F9263 | 11,3 | 1 11 | TMV0505S | 1 | 1 | 1 | 11,3 | 11,3 | 11,3
Miscellaneous Parts | | | | | | | | | | | | Miscellaneous Parts
20k | S64Y | 3 | 3 | 6 | Multi-turn trimpot, 64Y footprint | 67F5850 | 2,89 | 1 | CT94Y203-ND | 1,57 | 1 | | 20k | 3 | 3 | 6 | 8,67 | 8,67 | 17,34 | 3 | 3 | 6 | 4,71 | 4,71 | 9,42
22µH | R-12,5 | 3 | 3 | 3 | SRF > 13MHz, Imax > 285mA, 12.5mm pitch | 50H2891 | 0,2 | 1 | DN41223-ND | 1,33 | 1 | 22µH | 3 | 3 | 3 | 0,6 | 0,6 | 0,6 | 3 | 3 | 3 | 3,99 | 3,99 | 3,99
7.3728MHz | HC49/S | 1 | | 1 | 1 HC49 or equivalent package. | 18C1524 | 0,546 | 1 1 | X019-ND | 0,64 | 1 | 7.3728MHz | 1 | | 1 | 1 | 0,546 | | 0,546 | 0,546 | 1 | | 1 | 1 | 0,64 | | 0,64 | 0,64
PINHD-2X17 | 2X17 | 1 | 1 | 2 | 3 2x17 pin-header / ribbon cable connector | 90F4239 | 2,87 | 1 | 1-103186-7-ND | 2,46 | 1 4 | PINHD-2X17 | 1 | 1 | 2 | 3 | 2,87 | 2,87 | 5,74 | 8,61 | 1 | 1 | 2 | 3 | 2,46 | 2,46 | 4,92 | 7,38
PINHD-2X5 | 2X05 | 1 | | 1 | 1 2x5 pin-header / ribbon cable connector | 95F1805 | 2,14 | 1 | 103240-5-ND | 0,78 | 1 | PINHD-2X5 | 1 | | 1 | 1 | 2,14 | | 2,14 | 2,14 | 1 | | 1 | 1 | 0,78 | | 0,78 | 0,78
Sockets | | | | | | | | | Sockets
8-pin socket | DIL-08 | 2 | 6 | 8 | 14 | 25C3677 | 0,06 | 1 | 8-pin socket | 2 | 6 | 8 | 14 | 0,12 | 0,36 | 0,48 | 0,84
16-pin socket | DIL-16 | 1 | | 1 | 1 | 03C3508 | 0,121 | 1 | 16-pin socket | 1 | | 1 | 1 | 0,121 | | 0,121 | 0,121
28-pin socket | DIL-28 | 1 | 1 | 1 | 7.68mm wide. | 26C0566 | 0,276 | 1 | 28-pin socket | 1 | 1 | 1 | 0,16 | 0,276 | 0,276
Socket strip | SIL-20 | | | | Can be useful... | | | | Socket strip

Notes

Crystal and loading capacitors (Cxtal)
The crystal's loading capacitors must be chosen appropriately. Set Cxtal = (Cload - Cstray) * 2
Cload (crystal loading capacitance) is given in the crystal data sheet. Cstray is stray capacitance on the PCB + microcontroller. Estimate Cstray = 3 - 5pF.

47uF 1 ohm capacitor
This capacitor is hard to locate in through-hole form (unless you order from Newark) You can replace it with an SMD type.
Mount an SMD like this: Solder the negative end to its pad. Have the positive end land on the ground plane. Scrape off the solder mask
in front of the positive end and solder.
Also note that any ESR = 0.8 ohm to 1.2 ohm is acceptable.

Microcontroller
The AT90S4433 is "not recommended for new designs" which is industry-speak for "we are not going to manufacture this part for much longer". The replacement is the ATmega8. However, it has a problem associated with it:
ADC channels 5 and 6 are only 8 bit, while the EEG board is designed with 10 bit resolution in mind. (Channels 1 - 4 are ok though.)

TLC277 amplifier
In a four channel EEG setup (two amplifier boards), you only mount IC201 on one board.

DCDC converter
TMV0505S is not available in many places. It can be replaced with NMV0505SA. This converter has a rather high output voltage (6-7 V) at very light loads. Therefore, when building the digital board, mount all parts except the microcontroller. Turn on the power and measure the voltage in the +5V/3 net, e.g. at IC103 pin 8. The voltage should be LESS than 6V. If not, you must reduce the value of R127 (near the LED), in order to present the DCDC converter with a higher load.

Pin headers
These are fairly expensive at RS (order code 531-942, you need 17x2 + 17x2 + 3x2 = 74 pins total) so try to find them elsewhere.
You need 2.54mm pitch double-row headers or equialent connectors, for ribbon cable. The ribbon cable can be made from an old floppy-drive cable.

Socket strip
Instead of soldering wires directly to the PCB's you can solder in socket strips which you have cut into suitable lengths.
Then insert the wires into the sockets without soldering, during the testing phase. This way you do not risk breaking the wires before putting everything securely in a box. (Then you should solder them in.) 0.5mm diameter single-strand wire is suitable.

Reichelt notes
1) Crystal loading capacitance is 32pF so Cxtal = 56pF (estimate Cstray = 4pF)
2) Higher grade is available: INA114BP which costs €13.60. Note that for this application this is hardly needed.
3) The MAX232 listed does not have ESD protected I/O pins. Protected type has part no MAX232 ECPE and costs €4.80.
4) Two 14-pin sockets

RS components notes
Prices were calculated from SEK to Euros by dividing by ten but at the time of writing 1 EUR = 9 SEK. Also, VAT is not included.
1) Crystal loading capacitance is 7pF so Cxtal = 10pF (estimate Cstray = 5 pF)
2) Avoid buying these parts from here. They are more expensive than they need to be.
3) TMV0505S is replaced by NMV0505SA

Newark Electronics notes
1) Crystal loading capacitance is 20pF so Cxtal = 33pF (estimate Cstray = 4pF)
2) The part has 2.5mm lead pitch - bend to 5mm
3) The part has 5mm lead pitch rather than 10mm. C220 can be mounted two ways. The lower placement (seen PCB layout) is the correct one.
4) This part may be replaced with a small aluminium electroytic. Part no 18C4465 for $0.063
5) Digital board capacitors can be replaced by an aluminium electrolytics. This may degrade noise immunity. (Probably not). Part no 18C4469 for $0.147
6) ESR=1.2 Ohm. Can be replaced with an ESR=1.0 Ohm type. Part no 87F5155 for $4.78
7)
8)
9) Higher grade INA114BP is available. Part no 35C1716 for $12.08
10) A cheaper alternative is MAX232 CPE that lacks ESD protection. Part no 34C3833 for $2.91
11) TMV0505S is replaced by NMV0505SA

Digi-Key notes
1) Carbon resistor for possibly improved ESR protection
2) Can be replaced with the newer generation ATMEGA8-16PI-ND $6.33 see Microcontroller note above.
3) Higher grade: INA114BP-ND $10.28
4) Or S2212-17-ND tin $1.77 - a special order item

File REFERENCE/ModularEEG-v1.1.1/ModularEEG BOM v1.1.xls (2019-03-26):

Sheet: Parts list
ModularEEG v1.1.0 - Bill of Materials
Digital board
Qty | Value | Package | Parts
Capacitors
1 | 27pF C0G | C-5 | C102
2 | Cxtal | C-5 | C115 | C116
3 | 10nF X7R | C-5 | C108 | C113 | C119
7 | 100nF X7R | C-5 | C110 | C111 | C114 | C117 | C121 | C124 | C125 | C131
6 | 220nF 5% | C-5 | C103 | C104 | C105 | C106 | C107 | C109
2 | 1µF tantalum | EL25B | C122 | C123
6 | 10µF tantalum | EL25B | C101 | C120 | C126 | C127 | C128 | C129
3 | 47µF tantalum | EL25B | C112 | C118 | C130
Resistors
1 | 100R | R-10 | R111
12 | 470R | R-10 | R107 | R114 | R115 | R116 | R117 | R118 | R119 | R120 | R121 | R122 | R124 | R128
5 | 1k | R-10 | R125 | R126 | R127 | R129 | R130
6 | 7.5k | R-10 | R104 | R106 | R109 | R110 | R112 | R113
1 | 9k1 | R-10 | R103
3 | 10k | R-10 | R101 | R105 | R123
1 | 15k | R-10 | R102
Discrete Semiconductors
3 | 1N5818 | D-12,5 | D101 | D103 | D104
1 | LED 5mm | LED5 | D102
Integrated Circuits
2 | 6N139 | DIL-08 | IC103 | IC104
1 | 7805 | 78XXL_S | IC107
1 | AT90S4433P | DIL-28/3 | IC102
1 | MAX232 | DIL-16 | IC106
1 | TL431CLP | TO92-CLP | IC101
1 | TMV0505S | TMADCDC | IC105
Miscellaneous Parts
1 | 7.3728MHz | HC49/S | X101
3 | 22µH | R-12,5 | L101 | L102 | L103
1 | PINHD-2X5 | 2X05 | J101
1 | PINHD-2X17 | 2X17 | J102
Analog board
Qty | Value | Package | Parts
Capacitors
2 | 10pF C0G | C-5 | C209 | C210
4 | 100pF C0G | C-5 | C204 | C205 | C206 | C207
6 | 1nF X7R | C-5 | C212 | C216 | C222 | C224 | C232 | C233
2 | 10nF X7R | C-5 | C202 | C203
2 | 33nF 5% | C-5 | C234 | C236
12 | 100nF X7R | C-5 | C208 | C211 | C214 | C215 | C217 | C218 | C219 | C223 | C225 | C226 | C227 | C230
2 | 220nF 5% | C-5 | C231 | C235
4 | 1µF film | C-10 | C220 | C221 | C228 | C229
1 | 47µF tantalum | EL25B | C213
1 | 47µF tan 1ohm | ES-5 | C201
Resistors
1 | 100R | R-10 | R240
2 | 1k | R-10 | R220 | R222
16 | 2k2 | R-10 | R201 | R202 | R203 | R204 | R205 | R206 | R207 | R208 | R209 | R210 | R211 | R212
 |  |  | R214 | R215 | R216 | R217
2 | 8.2k | R-10 | R229 | R234
6 | 10k | R-10 | R218 | R219 | R232 | R237 | R238 | R239
2 | 15k | R-10 | R228 | R233
4 | 100k | R-10 | R221 | R225 | R230 | R235
1 | 200k | R-10 | R213
6 | 1M | R-10 | R223 | R224 | R226 | R227 | R231 | R236
Discrete Semiconductors
4 | BC547 | TO92 | Q205 | Q206 | Q207 | Q208
4 | BC557 | TO92 | Q201 | Q202 | Q203 | Q204
Integrated Circuits
2 | INA114P | DIL-08 | IC202 | IC203
4 | TLC277P | DIL-08 | IC201 | IC204 | IC205 | IC206
Miscellaneous Parts
3 | 20k | S64Y | P201 | P202 | P203
1 | PINHD-2X17 | 2X17 | J201
170

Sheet: Order info
ModularEEG v1.1.0 - ordering information
All prices as of September 2002.
Color key:
See notes below. |  |  |  |  |  | No part is selected.
See distributor-specific notes below.. |  |  |  |  |  | Not available. Prices given are estimates.
 |  |  |  |  |  |  | Reichelt |  |  |  | RS Components |  |  |  | Newark Electronics |  |  |  | Digi-Key (USD) |  |  |  |  | Reichelt |  |  |  |  |  |  |  | RS Components |  |  |  |  |  |  |  | Newark Electronics |  |  |  |  |  |  |  | Digi-Key
Value | Package | Qty D | Qty A | Qty D+A | Qty D+2A | Part requirements and notes | Part no. | Unit Price | Min Qty | ? | Part no. | Unit Price | Min Qty | ? | Part no. | Unit Price | Min Qty | ? | Part no. | Unit Price | Min Qty | ? |  | Qty D | Qty A | Qty D+A | Qty D+2A | Price D | Price A | Price D+A | Price D+2A | Qty D | Qty A | Qty D+A | Qty D+2A | Price D | Price A | Price D+A | Price D+2A | Qty D | Qty A | Qty D+A | Qty D+2A | Price D | Price A | Price D+A | Price D+2A | Qty D | Qty A | Qty D+A | Qty D+2A
Capacitors |  |  |  |  |  |  |  |  |  |  |  |  |  |  |  |  |  |  |  |  |  |  | Capacitors
10pF C0G | C-5 |  | 2 | 2 | 4 | 100V, 5mm pitch,C0G | Kerko-500 10p | 0.07 | 1 |  | N/A | 0.1 | 5 |  | 50N1022 | 0.044 | 1 |  |  |  |  |  | 10pF C0G | 0 | 2 | 2 | 4 | 0 | 0.14 | 0.14 | 0.28 | 0 | 5 | 5 | 5 | 0 | 0.5 | 0.5 | 0.5 | 0 | 2 | 2 | 4 | 0 | 0.088 | 0.088 | 0.176 | 0 | 0 | 0 | 0
Cxtal C0G | C-5 | 2 |  | 2 | 2 | 5mm pitch, C0G. See notes. | Kerko-500 56p | 0.07 | 1 | 1 | N/A | 0.1 | 5 | 1 | 50N1028 | 0.044 | 1 | 1 |  |  |  |  | Cxtal C0G | 2 | 0 | 2 | 2 | 0.14 | 0 | 0.14 | 0.14 | 5 | 0 | 5 | 5 | 0.5 | 0 | 0.5 | 0.5 | 2 | 0 | 2 | 2 | 0.088 | 0 | 0.088 | 0.088 | 0 | 0 | 0 | 0
100pF C0G | C-5 |  | 4 | 4 | 8 | 100V, 5mm pitch, C0G | Kerko-500 100p | 0.07 | 1 |  | N/A | 0.1 | 5 |  | 50N1068 | 0.044 | 1 |  |  |  |  |  | 100pF C0G | 0 | 4 | 4 | 8 | 0 | 0.28 | 0.28 | 0.56 | 0 | 5 | 5 | 10 | 0 | 0.5 | 0.5 | 1 | 0 | 4 | 4 | 8 | 0 | 0.176 | 0.176 | 0.352 | 0 | 0 | 0 | 0
1nF X7R | C-5 |  | 6 | 6 | 12 | 200V, 5mm pitch, X7R | X7R-5 1,0n | 0.07 | 1 |  | 298-9028 | 0.14 | 5 |  | 87F4719 | 0.142 | 1 | 2 |  |  |  |  | 1nF X7R | 0 | 6 | 6 | 12 | 0 | 0.42 | 0.42 | 0.84 | 0 | 10 | 10 | 15 | 0 | 1.4 | 1.4 | 2.1 | 0 | 6 | 6 | 12 | 0 | 0.852 | 0.852 | 1.704 | 0 | 0 | 0 | 0
10nF X7R | C-5 | 3 | 2 | 5 | 7 | 100V, 5mm pitch, X7R | X7R-5 10n | 0.07 | 1 |  | 264-4832 | 0.16 | 5 |  | 87F4724 | 0.123 | 1 |  |  |  |  |  | 10nF X7R | 3 | 2 | 5 | 7 | 0.21 | 0.14 | 0.35 | 0.49 | 5 | 5 | 5 | 10 | 0.8 | 0.8 | 0.8 | 1.6 | 3 | 2 | 5 | 7 | 0.369 | 0.246 | 0.615 | 0.861 | 0 | 0 | 0 | 0
33nF 5% | C-5 |  | 2 | 2 | 4 | 5%, 5mm pitch, max 3.5mm wide | N/A | 0.1 | 1 |  | 312-1504 | 0.082 | 10 |  | 18C4841 | 0.236 | 1 |  |  |  |  |  | 33nF 5% | 0 | 2 | 2 | 4 | 0 | 0.2 | 0.2 | 0.4 | 0 | 10 | 10 | 10 | 0 | 0.82 | 0.82 | 0.82 | 0 | 2 | 2 | 4 | 0 | 0.472 | 0.472 | 0.944 | 0 | 0 | 0 | 0
100nF X7R | C-5 | 8 | 12 | 20 | 32 | 50V, 5mm pitch, X7R | X7R-5 100n | 0.12 | 1 |  | 264-4876 | 0.205 | 5 |  | 96F8771 | 0.122 | 1 |  |  |  |  |  | 100nF X7R | 8 | 12 | 20 | 32 | 0.96 | 1.44 | 2.4 | 3.84 | 10 | 15 | 20 | 35 | 2.05 | 3.075 | 4.1 | 7.175 | 8 | 12 | 20 | 32 | 0.976 | 1.464 | 2.44 | 3.904 | 0 | 0 | 0 | 0
220nF 5% | C-5 | 6 | 2 | 8 | 10 | 5%, 5mm pitch, max 3.5mm wide | N/A | 0.2 | 1 |  | 312-1475 | 0.139 | 10 |  | 95B5780 | 0.108 | 1 |  |  |  |  |  | 220nF 5% | 6 | 2 | 8 | 10 | 1.2 | 0.4 | 1.6 | 2 | 10 | 10 | 10 | 10 | 1.39 | 1.39 | 1.39 | 1.39 | 6 | 2 | 8 | 10 | 0.648 | 0.216 | 0.864 | 1.08 | 0 | 0 | 0 | 0
1µF film | C-10 |  | 4 | 4 | 8 | 5% tolerance, 10mm pitch | MKH100-10 1,0µ | 0.3 | 1 |  | 298-0188 | 0.349 | 5 |  | 95B5792 | 0.325 | 1 | 3 |  |  |  |  | 1µF film | 0 | 4 | 4 | 8 | 0 | 1.2 | 1.2 | 2.4 | 0 | 5 | 5 | 10 | 0 | 1.745 | 1.745 | 3.49 | 0 | 4 | 4 | 8 | 0 | 1.3 | 1.3 | 2.6 | 0 | 0 | 0 | 0
1µF tantalum | EL25B | 2 |  | 2 | 2 | 35V, 2.5mm pitch | TANTAL 1,0/35 | 0.15 | 1 |  | N/A | 0.2 | 1 |  | 50N905 | 0.235 | 1 |  |  |  |  |  | 1µF tantalum | 2 | 0 | 2 | 2 | 0.3 | 0 | 0.3 | 0.3 | 2 | 0 | 2 | 2 | 0.4 | 0 | 0.4 | 0.4 | 2 | 0 | 2 | 2 | 0.47 | 0 | 0.47 | 0.47 | 0 | 0 | 0 | 0
10µF tantalum | EL25B | 6 |  | 6 | 6 | 16V, 2.5mm pitch | TANTAL 10/16 | 0.22 | 1 |  | N/A | 0.2 | 1 |  | 50N883 | 0.459 | 1 | 4 |  |  |  |  | 10µF tantalum | 6 | 0 | 6 | 6 | 1.32 | 0 | 1.32 | 1.32 | 6 | 0 | 6 | 6 | 1.2 | 0 | 1.2 | 1.2 | 6 | 0 | 6 | 6 | 2.754 | 0 | 2.754 | 2.754 | 0 | 0 | 0 | 0
47µF tantalum | EL25B | 3 | 1 | 4 | 5 | > 6.3V, 2.5mm pitch | TANTAL 47/6,3 | 0.33 | 1 |  | N/A | 0.3 | 1 |  | 50N860 | 0.683 | 1 | 5 |  |  |  |  | 47µF tantalum | 3 | 1 | 4 | 5 | 0.99 | 0.33 | 1.32 | 1.65 | 3 | 1 | 4 | 5 | 0.9 | 0.3 | 1.2 | 1.5 | 3 | 1 | 4 | 5 | 2.049 | 0.683 | 2.732 | 3.415 | 0 | 0 | 0 | 0
47µF tan 1ohm | ES-5 |  | 1 | 1 | 2 | > 6.3V, 5mm pitch, ESR = 0.8 - 1.2 ohm | N/A | 3 | 1 |  | N/A | 3 | 1 |  | 95F4832 | 2.96 | 1 | 6 |  |  |  |  | 47µF tan 1ohm | 0 | 1 | 1 | 2 | 0 | 3 | 3 | 6 | 0 | 1 | 1 | 2 | 0 | 3 | 3 | 6 | 0 | 1 | 1 | 2 | 0 | 2.96 | 2.96 | 5.92 | 0 | 0 | 0 | 0
Resistors |  |  |  |  |  |  |  |  |  |  |  |  |  |  |  |  |  |  |  |  |  |  | Resistors
100R | R-10 | 1 | 1 | 2 | 3 | 1% metal film, 0.25W, 10mm pitch | METALL 100 | 0.08 | 1 |  | 148-269 | 0.044 | 10 |  | 84N1686 | 0.031 | 1 |  |  |  |  |  | 100R | 1 | 1 | 2 | 3 | 0.08 | 0.08 | 0.16 | 0.24 | 10 | 10 | 10 | 10 | 0.44 | 0.44 | 0.44 | 0.44 | 1 | 1 | 2 | 3 | 0.031 | 0.031 | 0.062 | 0.093 | 0 | 0 | 0 | 0
470R | R-10 | 12 |  | 12 | 12 | 1% metal film, 0.25W, 10mm pitch | METALL 470 | 0.08 | 1 |  | 148-427 | 0.044 | 10 |  | 84N1765 | 0.031 | 1 |  |  |  |  |  | 470R | 12 | 0 | 12 | 12 | 0.96 | 0 | 0.96 | 0.96 | 20 | 0 | 20 | 20 | 0.88 | 0 | 0.88 | 0.88 | 12 | 0 | 12 | 12 | 0.372 | 0 | 0.372 | 0.372 | 0 | 0 | 0 | 0
1k | R-10 | 5 | 2 | 7 | 9 | 1% metal film, 0.25W, 10mm pitch | METALL 1,00K | 0.08 | 1 |  | 148-506 | 0.044 | 10 |  | 84N1712 | 0.031 | 1 |  |  |  |  |  | 1k | 5 | 2 | 7 | 9 | 0.4 | 0.16 | 0.56 | 0.72 | 10 | 10 | 10 | 10 | 0.44 | 0.44 | 0.44 | 0.44 | 5 | 2 | 7 | 9 | 0.155 | 0.062 | 0.217 | 0.279 | 0 | 0 | 0 | 0
2k2 | R-10 |  | 16 | 16 | 32 | 1% metal film, 0.25W, 10mm pitch | METALL 2,20K | 0.08 | 1 |  | 148-584 | 0.044 | 10 |  | 84N1737 | 0.031 | 1 |  |  |  |  |  | 2k2 | 0 | 16 | 16 | 32 | 0 | 1.28 | 1.28 | 2.56 | 0 | 20 | 20 | 40 | 0 | 0.88 | 0.88 | 1.76 | 0 | 16 | 16 | 32 | 0 | 0.496 | 0.496 | 0.992 | 0 | 0 | 0 | 0
7.5k | R-10 | 6 |  | 6 | 6 | 1% metal film, 0.25W, 10mm pitch | METALL 7,50K | 0.08 | 1 |  | 148-708 | 0.044 | 10 |  | 84N1794 | 0.031 | 1 |  |  |  |  |  | 7.5k | 6 | 0 | 6 | 6 | 0.48 | 0 | 0.48 | 0.48 | 10 | 0 | 10 | 10 | 0.44 | 0 | 0.44 | 0.44 | 6 | 0 | 6 | 6 | 0.186 | 0 | 0.186 | 0.186 | 0 | 0 | 0 | 0
8.2k | R-10 |  | 2 | 2 | 4 | 1% metal film, 0.25W, 10mm pitch | METALL 8,20K | 0.08 | 1 |  | 148-714 | 0.044 | 10 |  | 84N1799 | 0.031 | 1 |  |  |  |  |  | 8.2k | 0 | 2 | 2 | 4 | 0 | 0.16 | 0.16 | 0.32 | 0 | 10 | 10 | 10 | 0 | 0.44 | 0.44 | 0.44 | 0 | 2 | 2 | 4 | 0 | 0.062 | 0.062 | 0.124 | 0 | 0 | 0 | 0
9k1 | R-10 | 1 |  | 1 | 1 | 1% metal film, 0.25W, 10mm pitch | METALL 9,10K | 0.08 | 1 |  | 148-720 | 0.044 | 10 |  | 84N1804 | 0.031 | 1 |  |  |  |  |  | 9k1 | 1 | 0 | 1 | 1 | 0.08 | 0 | 0.08 | 0.08 | 10 | 0 | 10 | 10 | 0.44 | 0 | 0.44 | 0.44 | 1 | 0 | 1 | 1 | 0.031 | 0 | 0.031 | 0.031 | 0 | 0 | 0 | 0
10k | R-10 | 3 | 6 | 9 | 15 | 1% metal film, 0.25W, 10mm pitch | METALL 10,0K | 0.08 | 1 |  | 148-736 | 0.044 | 10 |  | 84N1687 | 0.031 | 1 |  |  |  |  |  | 10k | 3 | 6 | 9 | 15 | 0.24 | 0.48 | 0.72 | 1.2 | 10 | 10 | 10 | 20 | 0.44 | 0.44 | 0.44 | 0.88 | 3 | 6 | 9 | 15 | 0.093 | 0.186 | 0.279 | 0.465 | 0 | 0 | 0 | 0
15k | R-10 | 1 | 2 | 3 | 5 | 1% metal film, 0.25W, 10mm pitch | METALL 15,0K | 0.08 | 1 |  | 148-770 | 0.044 | 10 |  | 84N1702 | 0.031 | 1 |  |  |  |  |  | 15k | 1 | 2 | 3 | 5 | 0.08 | 0.16 | 0.24 | 0.4 | 10 | 10 | 10 | 10 | 0.44 | 0.44 | 0.44 | 0.44 | 1 | 2 | 3 | 5 | 0.031 | 0.062 | 0.093 | 0.155 | 0 | 0 | 0 | 0
100k | R-10 |  | 4 | 4 | 8 | 1% metal film, 0.25W, 10mm pitch | METALL 100K | 0.08 | 1 |  | 148-972 | 0.044 | 10 |  | 84N1685 | 0.031 | 1 |  |  |  |  |  | 100k | 0 | 4 | 4 | 8 | 0 | 0.32 | 0.32 | 0.64 | 0 | 10 | 10 | 10 | 0 | 0.44 | 0.44 | 0.44 | 0 | 4 | 4 | 8 | 0 | 0.124 | 0.124 | 0.248 | 0 | 0 | 0 | 0
200k | R-10 |  | 1 | 1 | 2 | 1% metal film, 0.25W, 10mm pitch | METALL 200K | 0.08 | 1 |  | 149-054 | 0.044 | 10 |  | 84N1720 | 0.031 | 1 |  | OD204J-ND | 0.42 | 1 | 1 | 200k | 0 | 1 | 1 | 2 | 0 | 0.08 | 0.08 | 0.16 | 0 | 10 | 10 | 10 | 0 | 0.44 | 0.44 | 0.44 | 0 | 1 | 1 | 2 | 0 | 0.031 | 0.031 | 0.062 | 0 | 1 | 1 | 2
1M | R-10 |  | 6 | 6 | 12 | 1% metal film, 0.25W, 10mm pitch | METALL 1,00M | 0.08 | 1 |  | 149-228 | 0.044 | 10 |  | 84N1719 | 0.033 | 1 |  |  |  |  |  | 1M | 0 | 6 | 6 | 12 | 0 | 0.48 | 0.48 | 0.96 | 0 | 10 | 10 | 20 | 0 | 0.44 | 0.44 | 0.88 | 0 | 6 | 6 | 12 | 0 | 0.198 | 0.198 | 0.396 | 0 | 0 | 0 | 0
Discrete Semiconductors |  |  |  |  |  |  |  |  |  |  |  |  |  |  |  |  |  |  |  |  |  |  | Discrete Semiconductors
1N5818 | D-12,5 | 3 |  | 3 | 3 | Any 1A schottky should work. | 1N 5818 | 0.06 | 1 |  | 348-5505 | 0.12 | 1 |  | 09F4475 | 0.203 | 1 |  |  |  |  |  | 1N5818 | 3 | 0 | 3 | 3 | 0.18 | 0 | 0.18 | 0.18 | 3 | 0 | 3 | 3 | 0.36 | 0 | 0.36 | 0.36 | 3 | 0 | 3 | 3 | 0.609 | 0 | 0.609 | 0.609 | 0 | 0 | 0 | 0
BC547 | TO92 |  | 4 | 4 | 8 | TO92 | BC 547B | 0.05 | 1 |  | 348-9399 | 0.043 | 1 |  | 92B7164 | 0.09 | 1 |  |  |  |  |  | BC547 | 0 | 4 | 4 | 8 | 0 | 0.2 | 0.2 | 0.4 | 0 | 4 | 4 | 8 | 0 | 0.172 | 0.172 | 0.344 | 0 | 4 | 4 | 8 | 0 | 0.36 | 0.36 | 0.72 | 0 | 0 | 0 | 0
BC557 | TO92 |  | 4 | 4 | 8 | TO92 | BC 557B | 0.05 | 1 |  | 348-9456 | 0.043 | 1 |  | 18C5843 | 0.1 | 1 |  |  |  |  |  | BC557 | 0 | 4 | 4 | 8 | 0 | 0.2 | 0.2 | 0.4 | 0 | 4 | 4 | 8 | 0 | 0.172 | 0.172 | 0.344 | 0 | 4 | 4 | 8 | 0 | 0.4 | 0.4 | 0.8 | 0 | 0 | 0 | 0
LED 5mm | LED5 | 1 |  | 1 | 1 | Any LED |  | 0.3 | 1 |  |  | 0.3 | 1 |  |  | 0.3 | 1 |  |  |  |  |  | LED 5mm | 1 | 0 | 1 | 1 | 0.3 | 0 | 0.3 | 0.3 | 1 | 0 | 1 | 1 | 0.3 | 0 | 0.3 | 0.3 | 1 | 0 | 1 | 1 | 0.3 | 0 | 0.3 | 0.3 | 0 | 0 | 0 | 0
Integrated Circuits |  |  |  |  |  |  |  |  |  |  |  |  |  |  |  |  |  |  |  |  |  |  | Integrated Circuits
6N139 | DIL-08 | 2 |  | 2 | 2 | Optocoupler | 6N139 | 0.69 | 1 |  | 303-135 | 1.18 | 1 |  | 09F7263 | 0.918 | 1 |  | 6N139QT-ND | 0.95 | 1 |  | 6N139 | 2 | 0 | 2 | 2 | 1.38 | 0 | 1.38 | 1.38 | 2 | 0 | 2 | 2 | 2.36 | 0 | 2.36 | 2.36 | 2 | 0 | 2 | 2 | 1.836 | 0 | 1.836 | 1.836 | 2 | 0 | 2 | 2
7805 | 78XXL_S | 1 |  | 1 | 1 | 5V regulator, >= 500mA. Size TO220 | µA 7805 | 0.28 | 1 |  | 633-026 | 0.575 | 1 |  | 34C1092 | 0.6 | 1 |  | LM7805CT-ND | 0.48 | 1 |  | 7805 | 1 | 0 | 1 | 1 | 0.28 | 0 | 0.28 | 0.28 | 1 | 0 | 1 | 1 | 0.575 | 0 | 0.575 | 0.575 | 1 | 0 | 1 | 1 | 0.6 | 0 | 0.6 | 0.6 | 1 | 0 | 1 | 1
AT90S4433P | DIL-28/3 | 1 |  | 1 | 1 | Will be replaced by ATmega8 soon. | AT 90S4433 PDIP | 7.5 | 1 |  | N/A | 7.5 | 1 |  | N/A | 6.62 | 1 |  | AT90S4433-8PI-ND | 6.62 | 1 | 2 | AT90S4433P | 1 | 0 | 1 | 1 | 7.5 | 0 | 7.5 | 7.5 | 1 | 0 | 1 | 1 | 7.5 | 0 | 7.5 | 7.5 | 1 | 0 | 1 | 1 | 6.62 | 0 | 6.62 | 6.62 | 1 | 0 | 1 | 1
INA114AP | DIL-08 |  | 2 | 2 | 4 | Low-power precision inamp | INA 114AP | 7.85 | 1 | 2 | 311-524 | 7.86 | 1 |  | 35C0480 | 8.02 | 1 | 9 | INA114AP-ND | 6.82 | 1 | 3 | INA114AP | 0 | 2 | 2 | 4 | 0 | 15.7 | 15.7 | 31.4 | 0 | 2 | 2 | 4 | 0 | 15.72 | 15.72 | 31.44 | 0 | 2 | 2 | 4 | 0 | 16.04 | 16.04 | 32.08 | 0 | 2 | 2 | 4
MAX232 | DIL-16 | 1 |  | 1 | 1 | RS232 tranceiver | MAX 232 CPE | 1 | 1 | 3 | 225-8510 | 1.74 | 1 |  | 34C3836 | 3.68 | 1 | 10 | 296-6940-5-ND | 2.2 | 1 |  | MAX232 | 1 | 0 | 1 | 1 | 1 | 0 | 1 | 1 | 1 | 0 | 1 | 1 | 1.74 | 0 | 1.74 | 1.74 | 1 | 0 | 1 | 1 | 3.68 | 0 | 3.68 | 3.68 | 1 | 0 | 1 | 1
TL431CLP | TO92-CLP | 1 |  | 1 | 1 | Adjustable voltage reference | TL 431 ACLP | 0.3 | 1 |  | 267-9995 | 0.39 | 1 |  | 08F9432 | 0.427 | 1 |  | 296-1290-ND | 0.56 | 1 |  | TL431CLP | 1 | 0 | 1 | 1 | 0.3 | 0 | 0.3 | 0.3 | 1 | 0 | 1 | 1 | 0.39 | 0 | 0.39 | 0.39 | 1 | 0 | 1 | 1 | 0.427 | 0 | 0.427 | 0.427 | 1 | 0 | 1 | 1
TLC277P | DIL-08 |  | 4 | 4 | 7 | Dual precision opamp | TLC 277 DIP | 1.65 | 1 |  | 428-464 | 1.785 | 1 |  | 08F9096 | 1.67 | 1 |  | 296-1828-5-ND | 1.55 | 1 |  | TLC277P | 0 | 4 | 4 | 7 | 0 | 6.6 | 6.6 | 11.55 | 0 | 4 | 4 | 7 | 0 | 7.14 | 7.14 | 12.495 | 0 | 4 | 4 | 7 | 0 | 6.68 | 6.68 | 11.69 | 0 | 4 | 4 | 7
TMV0505S | TMADCDC | 1 |  | 1 | 1 | 5Vin-5Vout 10% SIP7, 3kV iso | N/A | 10 | 1 |  | 192-0826 | 10.7 | 1 | 3 | 83F9263 | 11.3 | 1 | 11 |  |  |  |  | TMV0505S | 1 | 0 | 1 | 1 | 10 | 0 | 10 | 10 | 1 | 0 | 1 | 1 | 10.7 | 0 | 10.7 | 10.7 | 1 | 0 | 1 | 1 | 11.3 | 0 | 11.3 | 11.3 | 0 | 0 | 0 | 0
Miscellaneous Parts |  |  |  |  |  |  |  |  |  |  |  |  |  |  |  |  |  |  |  |  |  |  | Miscellaneous Parts
20k | S64Y |  | 3 | 3 | 6 | Multi-turn trimpot, 64Y footprint | 64Y-20K | 0.64 | 1 |  | 154-2448 | 1.476 | 1 |  | 67F5850 | 2.89 | 1 |  | CT94Y203-ND | 1.57 | 1 |  | 20k | 0 | 3 | 3 | 6 | 0 | 1.92 | 1.92 | 3.84 | 0 | 3 | 3 | 6 | 0 | 4.428 | 4.428 | 8.856 | 0 | 3 | 3 | 6 | 0 | 8.67 | 8.67 | 17.34 | 0 | 3 | 3 | 6
22µH | R-12,5 | 3 |  | 3 | 3 | SRF > 13MHz, Imax > 285mA, 12.5mm pitch | SMCC 22µ | 0.19 | 1 |  | 191-0526 | 0.225 | 10 |  | 50H2891 | 0.2 | 1 |  | DN41223-ND | 1.33 | 1 |  | 22µH | 3 | 0 | 3 | 3 | 0.57 | 0 | 0.57 | 0.57 | 10 | 0 | 10 | 10 | 2.25 | 0 | 2.25 | 2.25 | 3 | 0 | 3 | 3 | 0.6 | 0 | 0.6 | 0.6 | 3 | 0 | 3 | 3
7.3728MHz | HC49/S | 1 |  | 1 | 1 | HC49 or equivalent package. | 7,3728-HC49U-S | 0.49 | 1 | 1 | 311-811 | 1.23 | 1 | 1 | 18C1524 | 0.546 | 1 | 1 | X019-ND | 0.64 | 1 |  | 7.3728MHz | 1 | 0 | 1 | 1 | 0.49 | 0 | 0.49 | 0.49 | 1 | 0 | 1 | 1 | 1.23 | 0 | 1.23 | 1.23 | 1 | 0 | 1 | 1 | 0.546 | 0 | 0.546 | 0.546 | 1 | 0 | 1 | 1
PINHD-2X17 | 2X17 | 1 | 1 | 2 | 3 | 2x17 pin-header / ribbon cable connector | STIFTL. 2X17G | 0.21 | 1 |  |  |  |  | 2 | 90F4239 | 2.87 | 1 |  | 1-103186-7-ND | 2.46 | 1 | 4 | PINHD-2X17 | 1 | 1 | 2 | 3 | 0.21 | 0.21 | 0.42 | 0.63 | 0 | 0 | 0 | 0 | 0 | 0 | 0 | 0 | 1 | 1 | 2 | 3 | 2.87 | 2.87 | 5.74 | 8.61 | 1 | 1 | 2 | 3
PINHD-2X5 | 2X05 | 1 |  | 1 | 1 | 2x5 pin-header / ribbon cable connector | STIFTL. 2X17G | 0.21 | 1 |  |  |  |  | 2 | 95F1805 | 2.14 | 1 |  | 103240-5-ND | 0.78 | 1 |  | PINHD-2X5 | 1 | 0 | 1 | 1 | 0.21 | 0 | 0.21 | 0.21 | 0 | 0 | 0 | 0 | 0 | 0 | 0 | 0 | 1 | 0 | 1 | 1 | 2.14 | 0 | 2.14 | 2.14 | 1 | 0 | 1 | 1
Sockets |  |  |  |  |  |  |  |  |  |  |  |  |  |  |  |  |  |  |  |  |  |  | Sockets
8-pin socket | DIL-08 | 2 | 6 | 8 | 14 |  | GS 8 | 0.03 | 1 |  | Very expensive |  |  |  | 25C3677 | 0.06 | 1 |  |  |  |  |  | 8-pin socket | 2 | 6 | 8 | 14 | 0.06 | 0.18 | 0.24 | 0.42 | 0 | 0 | 0 | 0 | 0 | 0 | 0 | 0 | 2 | 6 | 8 | 14 | 0.12 | 0.36 | 0.48 | 0.84 | 0 | 0 | 0 | 0
16-pin socket | DIL-16 | 1 |  | 1 | 1 |  | GS 16 | 0.04 | 1 |  | since minimum |  |  |  | 03C3508 | 0.121 | 1 |  |  |  |  |  | 16-pin socket | 1 | 0 | 1 | 1 | 0.04 | 0 | 0.04 | 0.04 | 0 | 0 | 0 | 0 | 0 | 0 | 0 | 0 | 1 | 0 | 1 | 1 | 0.121 | 0 | 0.121 | 0.121 | 0 | 0 | 0 | 0
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

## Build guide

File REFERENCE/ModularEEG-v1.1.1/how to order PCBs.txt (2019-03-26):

PCB's are ordered from Olimex, located in Bulgaria.

This file contains ordering information for v1.1.
It is the latest version sent to Olimex for manufacture.

Price: (not including shipping): $23.40

Olimex charges for inital processing of the layouts. When a new revision of the ModularEEG is released, the price is $5 higher for the first person to order.

To order a set (1 analog + 1 digital) of PCBs, send an e-mail to Olimex <fastpcb@olimex.com> with the following info:

  Reference number: AR180903A
  Name:
  Email:
  Shipping address:
  Shipping option: Airmail

In return, you receive an e-mail with an order form in PDF format, which you should print, fill out, and fax back to them.

When the PCBs are shipped you will receive a notification e-mail. After that, delivery takes one to two weeks to most places.

Notes:

* If you already have a ModularEEG and want to add more channels, the Olimex reference number for a set of two analog boards is AR180903B.

* You will need a credit card (e.g VISA) so that they can charge you. Do *not* put the number in your e-mail. That is what the fax is for.

* You need to use a non-anonymous e-mail address, (i.e not Yahoo, Hotmail etc) because they have had trouble with credit card fraud.

See the Olimex web-site for shipping prices and other shipping options.

  http://olimex.com/pcb.html

Airmail costs $5 to destinations within Europe, and $8 to the rest of the world.

In short: Total cost will be max ~ $37 for whoever orders first, including $8 airmail. On reorders ~ $32.

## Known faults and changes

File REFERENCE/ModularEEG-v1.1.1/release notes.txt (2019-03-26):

Release Notes
-------------

To view the schematics and board layouts (.sch and .brd files),
download Eagle CAD from www.cadsoft.de
Eagle CAD runs on Linux as well as Windows.

Programming software and firmware info: see the ModularEEG zip-file.

Extras not included in the bill of materials:

* 34-pin ribbon cable (10-20cm of an old floppy-drive cable should work).
* Programming cable matching the 10-pin header on the ModularEEG. (see .zip file)
* Passthrough serial cable, and female DSUB connector.

* Battery connectors
* Battery

* Electrode connectors
* Electrodes
* Electrode cables
* Electrode paste and other accessories

* Optional: Enclosures.

It is recommended that you place the amplifier in a metal case, to reduce
electromagnetic interference.

You should NOT place the digital board in a metal case, because you can very
easily ruin the electrical isolation unless you know what you are doing.

Important postprocessing before making the modEEG pcbs

The modEEG pcbs are double sided with (plated through) vias and make heavy
use of "copper pouring".

Therefore the EAGLE *.brd files have to be postprocessed before printing in
the EAGLE CAD software with the "ratsnest" command.

Make sure Menu->options->set->misc->"Ratsnest processes polygones" is checked.

If the option is unchecked or no ratsnest is done, you do not get all the
important electrical connections that are implicitly done by the large so
called "copper pouring" polygons and the plated through vias - that are
electrical vertical connections from top to bottom layer.

Instead with "ratsnest" you get many thin yellow air-wires that indicate
missing connections between nodes (pins, pads) and would have to be soldered
manually if you should decide to use no copper pouring (what would be
absolutely no good idea!).

The openEEG developer teams decision to use double layer and copper pouring is
well founded, because it is essential for reduction of RF interference and
mains hum capacitively coupled into the circuit.

A modEEG built from pcbs without copper pouring after manual fixing all not
routed airwires (on both pcbs) will probably have sub optimal electrical
characteristics and performance (more noise and hum).

Change Log
----------
v1.1.1 - changes from v1.1.0
* Added postprocessing information to the release notes

v1.1.0 - changes from v1.0.0

* Replaced 10nF 5% capacitors with 1nF ceramic to increase AA-filter stability.
* Added placement markings for the 1uF caps on the amplifier board.
* Replaced Newark part number for 1MOhm resistors.
* Swapped top and bottom layers on the amplifier board.
* Added Newark part number for 22uH inductors.
* Added Olimex reference number for two analog boards (v1.0.0 layout)
* Added two mounting holes to the amplifier board
* Rewrote EEG connector labels
* Moved some connector labels into the silkscreen layer.
* Added Jake Stewart's cabling schematic
  (with edits - e.g text was too large in Eagle v4.09)

v1.0.0 - changes from v0.07:

* Changed to the standard versioning scheme: major.minor.bugfix
* Firmware is released separately from the schematics from now on.

* Changed D101 from BAT48 to 1N5818.

* Added a pin that makes it easier to connect the buffered common mode
  signals on different boards, to the single DRL amplifier.
  The pin is marked "COM" and is located near the DRL amplifier.
* Moved mounting screws on the analog board to opposite corners to
  increase the clearance around J201.
* Minor layout modifications on the boards, increasing the clearances
  around some capacitors.

* Clarified DRL trimming instructions on the schematic.
* Cleaned up the schematics some more.
* Cleaned up Cables.sch slightly.

v0.07 - changes from v0.06:

* Changed R124 and R128 (optocoupler LED-current limiters) to 470 ohms.
* Programming connector is now standard 10-pin.
* Cleaned up the digital board layout.
* 5VI 5VO power pins removed in favor of a single power input.
* Bugfix: digital board outline cut open to preserve isolation distances.
* Bugfix: Diode moved out from under 7805.
* 10k trimpots changed to 20k
* Added decoupling capacitor near optocoupler on isolated side.

v0.06 - changes from v0.05:

Important note:

Some parts from Newark did not fit the v0.04 / v0.05 PCBs so
the layout was modified for v0.06.

If you have a v0.05 board or earlier, the 1uF (both kinds), 10uF
and 47uF capacitors from Newark, may not fit on a v0.04 board.
The low-ESR 47uF capacitor may also be a tight fit.

The following three changes are what caused this:

* Layout change: Moved a few parts slightly to allow for bigger
  capacitors from Newark
* Layout change: Added holes (vias really) for 1uF capacitors with
  5mm lead pitch (from Newark).
* Layout change: Lead pitch for low ESR capacitor changed to 5 mm.

The other changes are:

* Added a "how to order PCBs.txt" file

* Change log bug. :o) These two changes were not mentioned in the
  previous change log entry:

  1 Added a "crowbar-diode" D104
    Only for those who will supply +5V from e.g a PS/2 port
    rather than using the on-board 7805.

  2 Added two 3mm mounting holes on each board.

* Modified the WARNING.txt file: Rewrote portions of the disclaimer
  for the ModularEEG, and split up some paragraphs to make them
  easier to read.
* Marked the programming-clock RC-network (C102, R108) as optional.
* Removed C102 from the order info spreadsheet.
* Remarked the crystal loading capacitors (C115, C116) as Cxtal.
* Fixed "missing junction" warnings in the schematics.

Complete BOM / order info overhaul:

* Added Newark Electronics (US) to the order info spreadsheet.
* Added partial Digi-Key (US) order info (to complement Newark)
* Modified inductor requirements: Increased Imax from 200mA to 285mA
  Actually ~200mA is ok, but is less than theoretical maximum.
* Added Cxtal calculation information.
* Reworked the notes.

v0.05 - changes from v0.04:

* Added missing 47uF capacitor in the BOM (you need 4, not 3)
* Added resistors missing in the BOM: R124 R125 R126 R127 R128 R129 R130 (all 1k)
* The v0.04 firmware read the ADC improperly, so no data was output.
* Change: New recommended ESR for C201 is 1 ohm.

  Recommended reference parts:

  Kemet T350K476K025AS or T356K476K025AS
  Digikey part no 399-1422-ND or 399-1347-ND
  47uF/25V, ESR = 1.0 ohm @ 100kHz.
  Lead pitch 5mm, price $5.07

  Note the 5mm lead pitch. The footprint on the PCB is not changed though.

v0.04 - changes from v0.03:

* Added a power-on LED.
* Removed secondary 7805. The DCDC converter is now required.
* Added a diode to protect the electronics from a reversed power supply.
* Added a 4th order lowpass filter, fc = 58Hz
* Switched to INA114 instrumentation amplifier.
* Gain changes: Second stage gain is 10 - 100, (G = 40 is the default).
  Filter gain is 16.
* Added 10k trimpot for subtracting common mode DC voltages in the DRL,
  caused by cheap inamps.

v0.03 - changes from v0.02

* New DC/DC converter footprint
* Fixed swapped component designators
* Bill of materials is rewritten.
* Added cabling schematics.
* Added new firmware source.

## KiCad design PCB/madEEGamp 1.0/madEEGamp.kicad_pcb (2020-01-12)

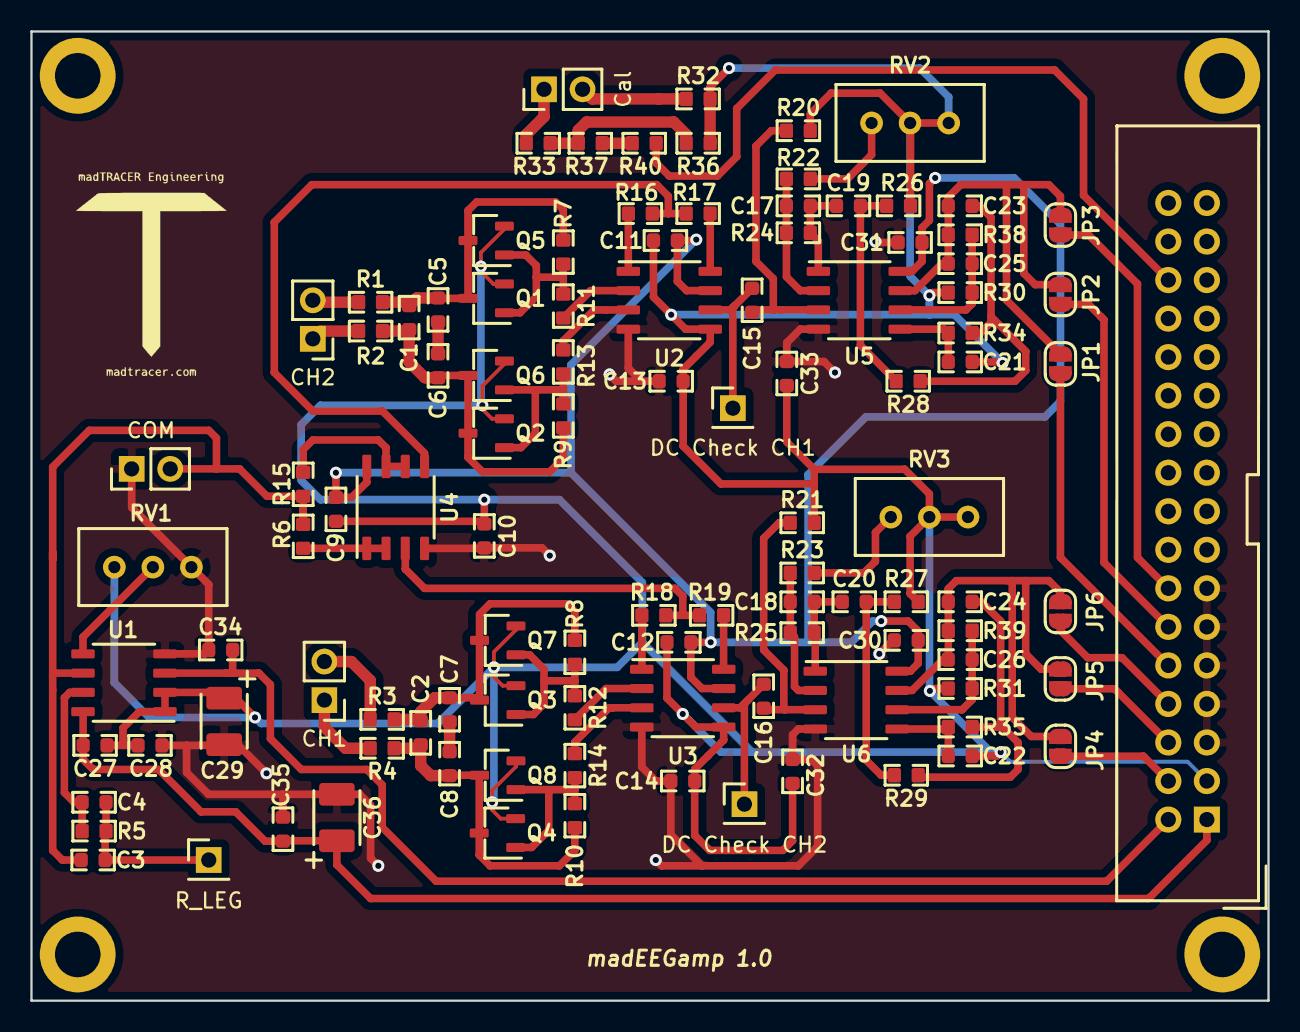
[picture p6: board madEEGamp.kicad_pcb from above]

Board: 2 copper layers, 81.5 x 63.9 mm, 107 parts (0 on the bottom side), 66 nets.

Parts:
C1, C2: 10pF; C_0603
C3, C4, C17, C18, C25, C26: 1nF; C_0603
C5, C6, C7, C8: 100pF; C_0603
C9, C10, C11, C12, C13, C14, C27, C28, C30, C31, C32, C33: 100nF; C_0603
C15, C16, C19, C20: 1μF; C_0603
C21, C22: 220nF 5%; C_0603
C23, C24: 33nF 5%; C_0603
C29: 47μF tan 1ohm; CP_EIA-3528-15_AVX-H
C34, C35: 10nF; C_0603
C36: 47μF; CP_EIA-3528-15_AVX-H
CH1: CH1; PinHeader_1x02_P2.54mm_Vertical
CH2: CH2; PinHeader_1x02_P2.54mm_Vertical
COM: COM; PinHeader_1x02_P2.54mm_Vertical
Cal: Cal; PinHeader_1x02_P2.54mm_Vertical
DC Check CH1: DC Check CH1; PinHeader_1x01_P2.54mm_Vertical
DC Check CH2: DC Check CH2; PinHeader_1x01_P2.54mm_Vertical
JP1, JP4: SJ201; SolderJumper-2_P1.3mm_Open_RoundedPad1.0x1.5mm
JP2, JP5: SJ202; SolderJumper-2_P1.3mm_Open_RoundedPad1.0x1.5mm
JP3, JP6: SJ203; SolderJumper-2_P1.3mm_Open_RoundedPad1.0x1.5mm
Q1, Q2, Q3, Q4: BC847; SOT-23
Q5, Q6, Q7, Q8: BC857; SOT-23
R1, R2, R3, R4, R7, R8, R9, R10, R11, R12, R13, R14, R16, R17, R18, R19: 2k2; R_0603
R5: 200k; R_0603
R6, R15, R28, R29, R32, R33: 10k; R_0603
R20, R21, R26, R27, R37, R40: 1M; R_0603
R22, R23: 1k; R_0603
R24, R25, R38, R39: 100k; R_0603
R30, R31: 8.2k; R_0603
R34, R35: 15k; R_0603
R36: 100; R_0603
RV1, RV2, RV3: 20k; BOURNS_3296W_Vertical
R_LEG: R_LEG; PinHeader_1x01_P2.54mm_Vertical
U1, U4, U5, U6: AD822; SOIC-8_3.9x4.9mm_P1.27mm
U2, U3: AD620; SOIC-8_3.9x4.9mm_P1.27mm
X7: PIN_HEADER_2X17_2.54; IDC-Header_2x17_P2.54mm_Vertical

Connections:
+5V: C9.2, C11.1, C12.1, C30.1, C31.1, U2.7, U3.7, U4.8, U5.8, U6.8
/ADIN0: C24.1, C26.1, JP4.2, JP5.2, JP6.2, R39.1, U6.7
/ADIN1: C23.1, C25.1, JP1.2, JP2.2, JP3.2, R38.1, U5.7
/CH1+: CH1.1, R4.2
/CH1-: CH1.2, R3.2
/CH2+: CH2.1, R2.2
/CH2-: CH2.2, R1.1
/PWM: R40.1, X7.30
/R_LEG: C3.2, C4.2, R5.2, R_LEG.1
/VGND: C9.1, C10.1, C11.2, C12.2, C13.2, C14.2, C21.2, C22.2, C27.2, C28.2, C29.1, C32.1, C33.1, Q1.2, Q2.2, Q3.2, Q4.2, Q5.2, Q6.2, Q7.2, Q8.2, R20.2, R21.2, R26.2, R27.2, R30.2, R31.2, R32.1, R36.1, RV1.1, RV2.2, RV2.3, RV3.2, RV3.3, U1.1, U1.2, U2.5, U3.5, X7.3
GNDA: C10.2, C13.1, C14.1, C28.1, C29.2, C30.2, C31.2, C32.2, C33.2, C34.2, C35.2, C36.2, COM.1, RV1.3, U1.4, U2.4, U3.4, U4.4, U5.4, U6.4, X7.5, X7.7, X7.9, X7.11, X7.13
unnamed: C1.1, C5.1, Q1.3, Q5.3, R1.2, R7.1
unnamed: C1.2, C6.2, Q2.3, Q6.3, R2.1, R9.2
unnamed: C2.1, C7.1, Q3.3, Q7.3, R3.1, R8.2
unnamed: C2.2, C8.2, Q4.3, Q8.3, R4.1, R10.2
unnamed: C3.1, COM.2, R6.2, R15.2, U1.6
unnamed: C4.1, R5.1, U1.7
unnamed: C5.2, C6.1
unnamed: C7.2, C8.1
unnamed: C15.1, R20.1, U5.3
unnamed: C15.2, DC Check CH1.1, U2.6
unnamed: C16.1, R21.1, U6.3
unnamed: C16.2, DC Check CH2.1, U3.6
unnamed: C17.1, R22.1, R24.2, U5.2
unnamed: C17.2, C19.2, R24.1, U5.1
unnamed: C18.1, R23.1, R25.2, U6.2
unnamed: C18.2, C20.2, R25.1, U6.1
unnamed: C19.1, R26.1, R28.2
unnamed: C20.1, R27.1, R29.2
unnamed: C21.1, R34.1, U5.5
unnamed: C22.1, R35.1, U6.5
unnamed: C23.2, R28.1, R34.2
unnamed: C24.2, R29.1, R35.2
unnamed: C25.2, R30.1, R38.2, U5.6
unnamed: C26.2, R31.1, R39.2, U6.6
unnamed: C27.1, C35.1, C36.1, U1.8, X7.1
unnamed: C34.1, U1.3, X7.2
unnamed: JP1.1, X7.10
unnamed: JP2.1, X7.12
unnamed: JP3.1, X7.14
unnamed: JP4.1, X7.4
unnamed: JP5.1, X7.6
unnamed: JP6.1, X7.8
unnamed: Q1.1, Q5.1, R7.2, R11.2
unnamed: Q2.1, Q6.1, R9.1, R13.2
unnamed: Q3.1, Q7.1, R8.1, R12.2
unnamed: Q4.1, Q8.1, R10.1, R14.2
unnamed: R6.1, U4.1, U4.2
unnamed: R11.1, U2.2
unnamed: R12.1, U3.2
unnamed: R13.1, U2.3
unnamed: R14.1, U3.3
unnamed: R15.1, U4.6, U4.7
unnamed: R16.1, U2.1
unnamed: R16.2, R17.2, U4.5
unnamed: R17.1, U2.8
unnamed: R18.1, U3.1
unnamed: R18.2, R19.2, U4.3
unnamed: R19.1, U3.8
unnamed: R22.2, RV2.1
unnamed: R23.2, RV3.1
unnamed: Cal.2, R32.2
unnamed: R33.1, R36.2, R37.2
unnamed: Cal.1, R33.2
unnamed: R37.1, R40.2
unnamed: RV1.2, U1.5

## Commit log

2019-03-26 Initial commit (ampPCB draft)
    [EEGamp.kicad_pcb, EEGamp.sch, ModularEEG BOM v1.1.xls, ModularEEG16Ch.brd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]
2019-03-27 Test points added
    [EEGamp.kicad_pcb, EEGamp.sch]
2019-03-27 Fixed unrouted track
    [EEGamp.kicad_pcb]
2020-01-07 Project reborn! =]
    [EEGamp.kicad_pcb, EEGamp.sch]
2020-01-12 madEEGamp 1.0 finished
    [madEEGamp.kicad_pcb, madEEGamp.sch]
2020-01-12 Ineractive BOM and Gerbers added for madEEGamp 1.0
    [EEGamp.kicad_pcb, madEEGamp-B_Cu.gbr, madEEGamp-B_Mask.gbr, madEEGamp-B_Paste.gbr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]
